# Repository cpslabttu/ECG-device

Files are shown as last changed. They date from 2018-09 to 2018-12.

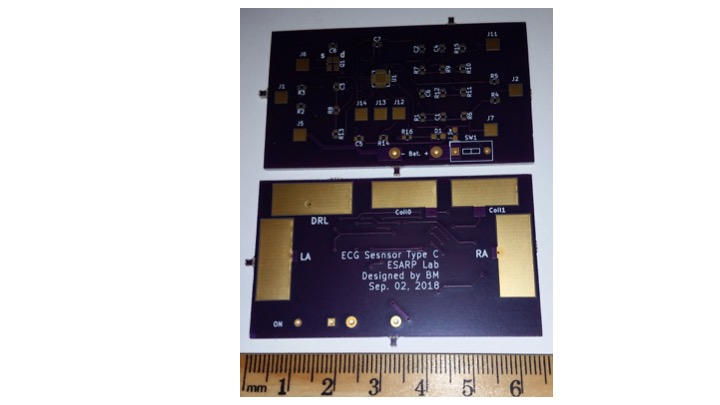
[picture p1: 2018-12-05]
Fig pcb.jpg

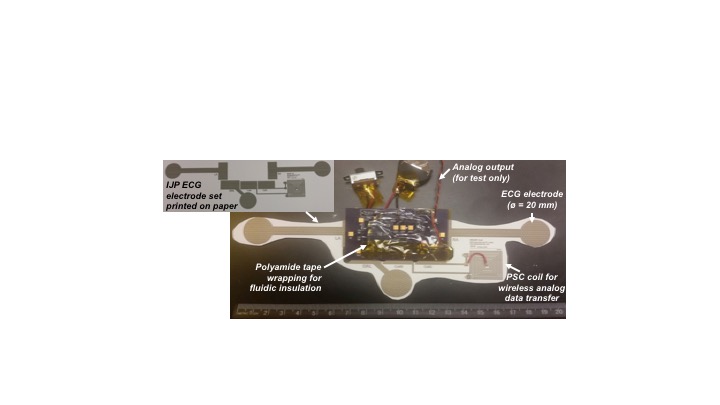
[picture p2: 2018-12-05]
Final ECG device TypeC ver1.jpeg

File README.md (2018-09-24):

# ECG-device-TypeC
Created by: Dr. B. I. Morshed, Assoc. Prof., EECE, University of Memphis, Memphis TN USA.

If using this project files, please cite:

B. I. Morshed, "Ultra Low-power Inductively Coupled Wearable ECG Sensor Design with Inkjet Printed Dry Electrodes", National Radio Science Meeting, Boulder, CO, 2019.

B. I. Morshed, B. Harmon, M. S. Zaman, M. J. Rahman, S. Afroz, and M. Rahman, "Inkjet Printed Fully-passive Body-worn Wireless Sensors for Smart and Connected Community (SCC)", J. Low Power Electron. Appl., vol. 7, no. 4, article 26, pp. 1-21, Nov. 2017.

Sergi Consul-Pacareu, and Bashir I. Morshed, "Design and analysis of a novel wireless resistive analog passive sensor technique", IET Wireless Sensor Systems, vol. 8, no. 2, pp. 45-51, 2018.

B. Noroozi and B. I. Morshed, "PSC Optimization of 13.56-MHz Resistive Wireless Analog Passive Sensors", IEEE Trans. Microwave Theory and Techniques, vol. 65, no. 9, pp. 3548-3555, Sept. 2017.

For project related info, please visit: http://www.memphis.edu/esarp/nsf_scc/index.php

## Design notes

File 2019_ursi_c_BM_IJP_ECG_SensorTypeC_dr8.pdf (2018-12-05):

# Ultra Low-power Inductively Coupled Wearable ECG Sensor Design with Inkjet Printed Dry Electrodes

Bashir I. Morshed
Electrical and Computer Engineering University of Memphis
Memphis, TN 38152 USA
bmorshed@memphis.edu

Abstract—Wearable Electrocardiogram (ECG) devices cannot be used for long duration due to power requirement (on a single charge) and electrode degradation. A new extremely low power wearable ECG sensor device is proposed in this work that minimizes power consumption by eliminating digitization and wireless data transfer with a zero power analog inductive coupling and long duration inkjet printed (IJP) dry electrodes. The prototyped device can operate on a coin cell for 140 hours consuming only 1.6 mA. Ability to collect ECG data at home for long duration can largely improve capabilities of mobile health (mHealth) towards Smart and Connected Communities (SCC).

I. INTRODUCTION
Electrocardiography (ECG/EKG) systems have progressed from large stationary bench setup to miniature wearable or body-worn systems [1]. Related challenges that are preventing further miniaturization include power consumption and long-time operation of ECG electrodes. Inkjet printing (IJP) is a new additive fabrication technology that can deposit materials (in ink form) to planar substrates (such as paper) with high precision (a few micron) achieving consistent thin film profile (in the range of micron). We have previously reported an IJP electrode for ECG data capture that operates for a long duration (several days) without degradation [2]. In this paper, we report a new design scheme for an ultra low-power wearable ECG sensor system that incorporates the IJP ECG electrodes.

II. CONCEPT
Fig. 1a shows a typical ECG sensor system that includes ECG electrodes, differential amplifier followed by filter and other analog signal processing circuitry (e.g. variable gain amplifier), an analog-to-digital converter (ADC), an optional microcontroller unit (MCU) for data buffer and management of the wireless module, and a wireless module (typically Bluetooth or BLE). In addition, if the circuit is powered with rechargeable battery (e.g. LiPo), a charge management circuitry will be needed (not shown).
Fig. 1b also shows the proposed ECG sensor system that eliminates the most power hungry element: the wireless module. Typical Bluetooth module requires 50 - 70 mA current during transmission which might be an order higher compared to other modules on the wearable ECG sensor system. Instead of the typical wireless module, we have used inductive loading principle that is developed through our Wireless Resistive Analog Sensor (WRAP) sensor research work [3,4]. Inductive loading technique does not consume any power from the sensor itself, hence leads to a low-power design. Furthermore, data through inductive loading can be transferred in analog mode (e.g. amplitude modulation), which also eliminates the need for the ADC and MCU. However, a voltage-to-impedance transducer is needed to interface the analog output and the transmitter coil, when we have realized with a single transistor.

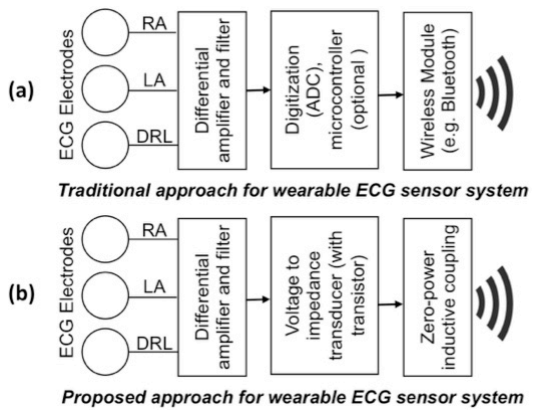
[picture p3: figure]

Fig. 1. (a) Traditional wearable ECG sensor system. (b) The proposed ECG sensor system.

III. DESIGN DESCRIPTION
Fig. 2 shows the complete KiCad schematic circuit diagram of the prototyped ECG sensor. Note that the planar spiral coil (PSC) and ECG electrodes are not part of KiCad schematic and are shown for illustration purpose only. The designed KiCad EDA files (schematic, layout, and gerber) are made open access via Github (https://github.com/esarplab/ECG-device).

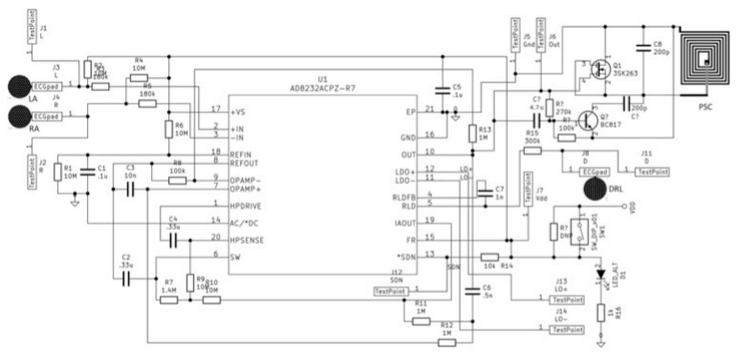
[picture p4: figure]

Fig. 2. Schematic diagram of the proposed ECG sensor. The differential amplifier, filter, and gain is performed with a commercial single-lead analog front end (AFE) integrated chip (AD8232, Analog Devices Inc.). AD8232 amplifies the ECG signals from the electrodes using the internal Instrument Amplifier (IA) and filters. The output can be applied to either a MOSFET (depletion mode) [4] or a BJT amplifier [3]. The results here are only based on the BJT amplifier. The transistor acts as a resistive load to the PSC coil for inductive coupling. The inductive coupling is probed with a scanner device (not shown here) that transmits ISM band RF signal (7 - 13.56 MHz). The modulation of envelope of the carrier signal is captured by the scanner [3].
The schematic design was used to develop a 2-layer PCB using KiCad as shown in Fig. 3. The top layer contained all the components and testpads, while the bottom layer contained 5 exposed copper plates that allow direct taping of the IJP electrodes and the PSC printed on paper. The PCB design was fabricated via Oshpark 2-layer PCB service (Oshpark LLC).

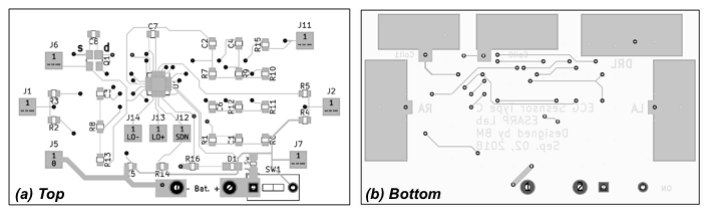
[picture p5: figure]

Fig. 3. Layout of the PCB: (a) Top layer and (b) Bottom layer. The IJP electrodes were printed with Ag nanoparticle ink (B25, Novacentrix) using an IJP printer (DMP2831, FujiFilm Dimatix Inc.) on the glossy side of a 10.4 mil photopaper (Kirkland Signature, Costco). We have previously reported details of this IJP dry electrodes [2] and PSC design [5]. The complete IJP layout contains 3 ECG electrodes (LA, RA, and DRL) and a PSC coil. We have spaced LA and RA ECG electrodes by 20 cm, but this can be easily modified and customized as per individual and ECG Lead need. This ease of personalized customization is an added advantage of the IJP process. The layout also contains the pads corresponding to the bottom layer of the PCB and attached using polyamide tape. The populated PCB with IJP electrodes and coil, along with a coin cell battery and a switch weighs only 17.9 grams (Fig. 4).

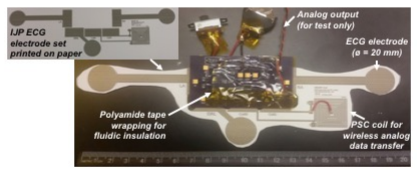
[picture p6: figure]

Fig. 4. A photograph of the fabricated and populated ECG sensor PCB attached with IJP electrodes and PSC on paper.

IV. RESULTS
The prototyped ECG device was tested and verified to collect ECG data from finger and chest configurations. Fig. 5 shows a set of data from chest configuration. The signal shows interference from utility line noise, which is removed with a 6th order Butterworth Low pass filter with fc = 40 Hz (Fig. 6). The inductively coupled signal also need and inversion operation as the envelope signal is inverted related to ECG output signal. The current consumption of the proposed ECG sensor system is only 1.6 mA, which allows a CR2032 (3V Lithium coin cell battery) to continuously operate for 140 hrs.

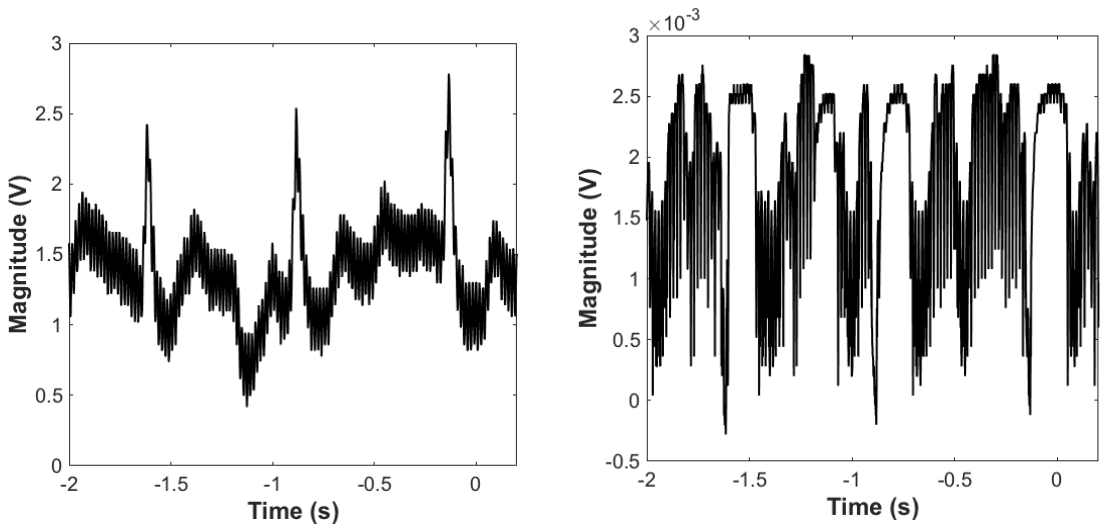
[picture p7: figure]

Fig. 5. A segment of ECG signals from the analog output (left) and from the inductively coupled envelope detector (right).

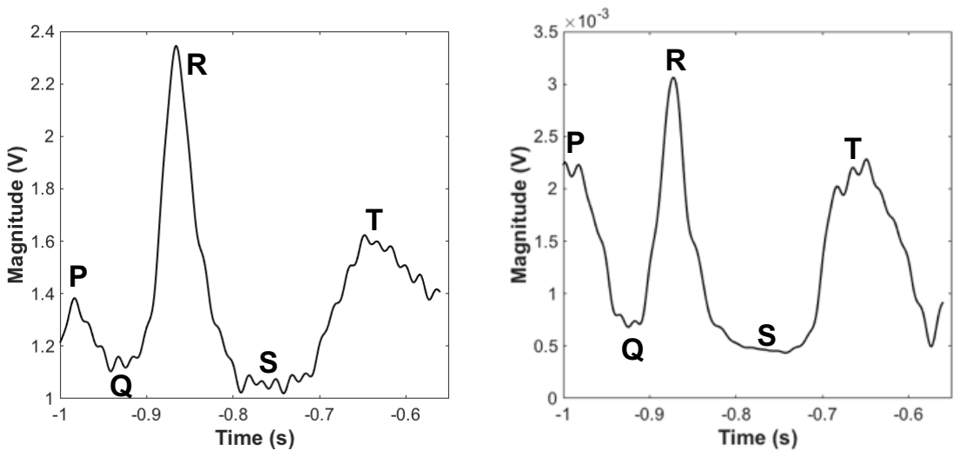
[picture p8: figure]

Fig. 6. An ECG beat from the analog output (left) and the inductively coupled signal (right) after signal processing.

V. CONCLUSIONS
We report an ultra low-power wearable ECG sensor design that uses zero-power inductive coupling and eliminates digitization and wireless transmission. We have demonstrated the prototype with IJP dry ECG electrodes to collect signals for long durations. Future work will improve the signal quality, minimize nonlinearity, optimize design, and reduce noise.

ACKNOWLEDGEMENT
This material is based upon work supported by the National Science Foundation under Grant No. 1637250 and FIT Foundation Fund Technology Development Grant 20715.

REFERENCES
[1] Y. Zheng, et al. “Unobtrusive Sensing and Wearable Devices for Health Informatics”, IEEE Trans Biomedical Engineering, vol. 61, no. 5, pp. 1538-1554, May 2014.
[2] A. Mohapatra, B. I. Morshed, S. Shamsir, and S. K. Islam, "Inkjet Printed Thin Film Electronic Traces on Paper for Low-cost Body-worn Electronic Patch Sensors", IEEE conf Body Sensor Networks (BSN), Las Vegas, NV, pp. 169-172, 2018.
[3] B. I. Morshed, B. Harmon, M. S. Zaman, M. J. Rahman, S. Afroz, and
M. Rahman, "Inkjet Printed Fully-passive Body-worn Wireless Sensors for Smart and Connected Community (SCC)", J. Low Power Electron. Appl., vol. 7, no. 4, article 26, pp. 1-21, Nov. 2017.
[4] S. Consul-Pacareu, and B. I. Morshed, "Design and analysis of a novel wireless resistive analog passive sensor technique", IET Wireless Sensor Systems, vol. 8, no. 2, pp. 45-51, 2018.
[5] B. Noroozi and B. I. Morshed, "PSC Optimization of 13.56-MHz Resistive Wireless Analog Passive Sensors", IEEE Trans. Microwave Theory and Techniques, vol. 65, no. 9, pp. 3548-3555, Sept. 2017.

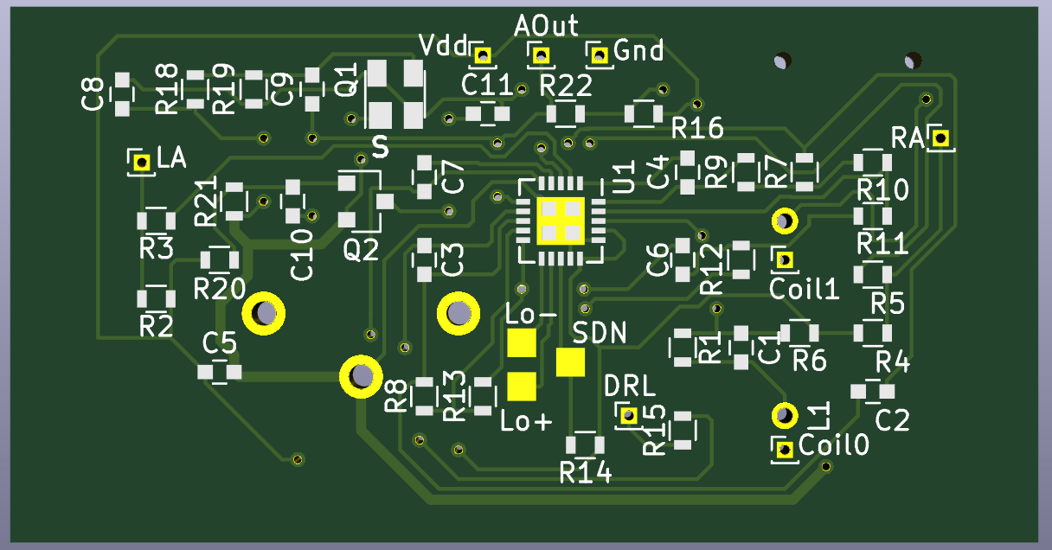
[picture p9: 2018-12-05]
ECGtypeC_V2 layout top3D.png

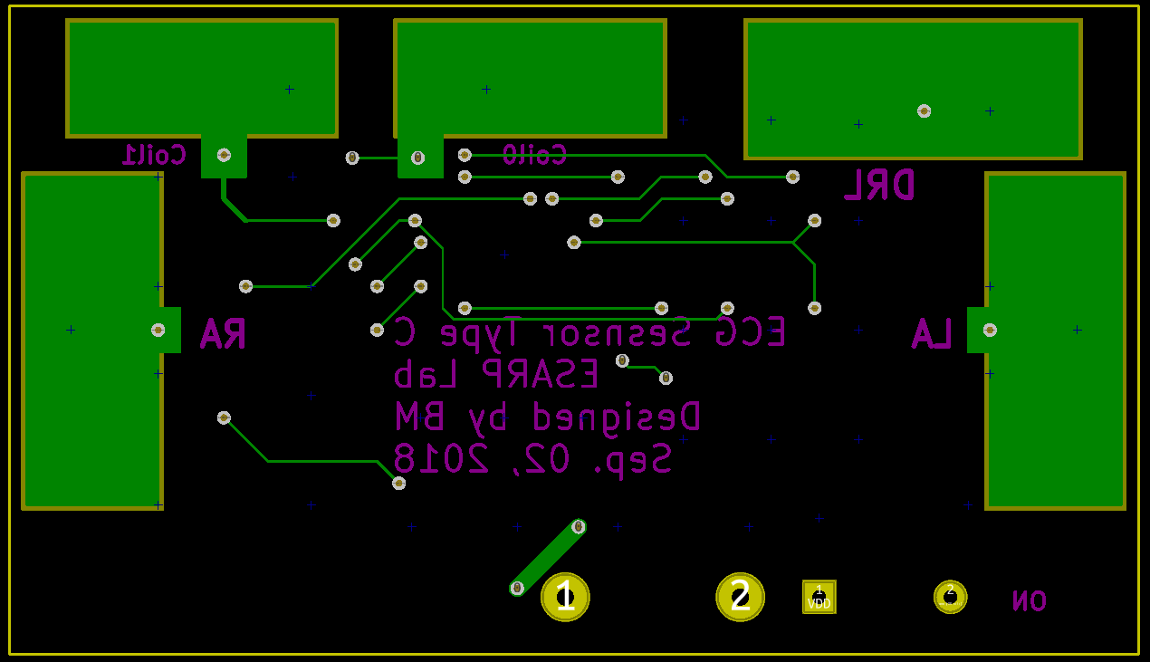
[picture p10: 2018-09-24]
ECGtypeC_layout bot.png

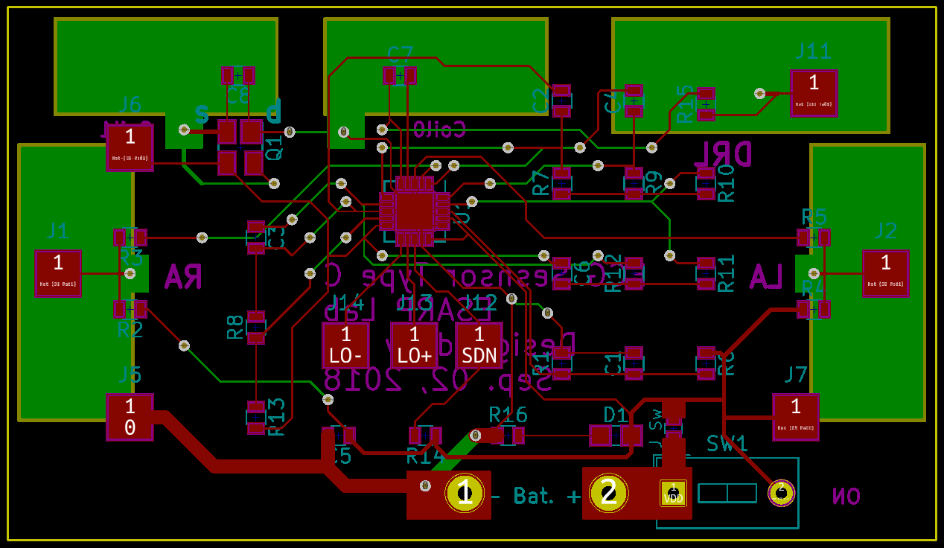
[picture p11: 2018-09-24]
ECGtypeC_layoutall.png

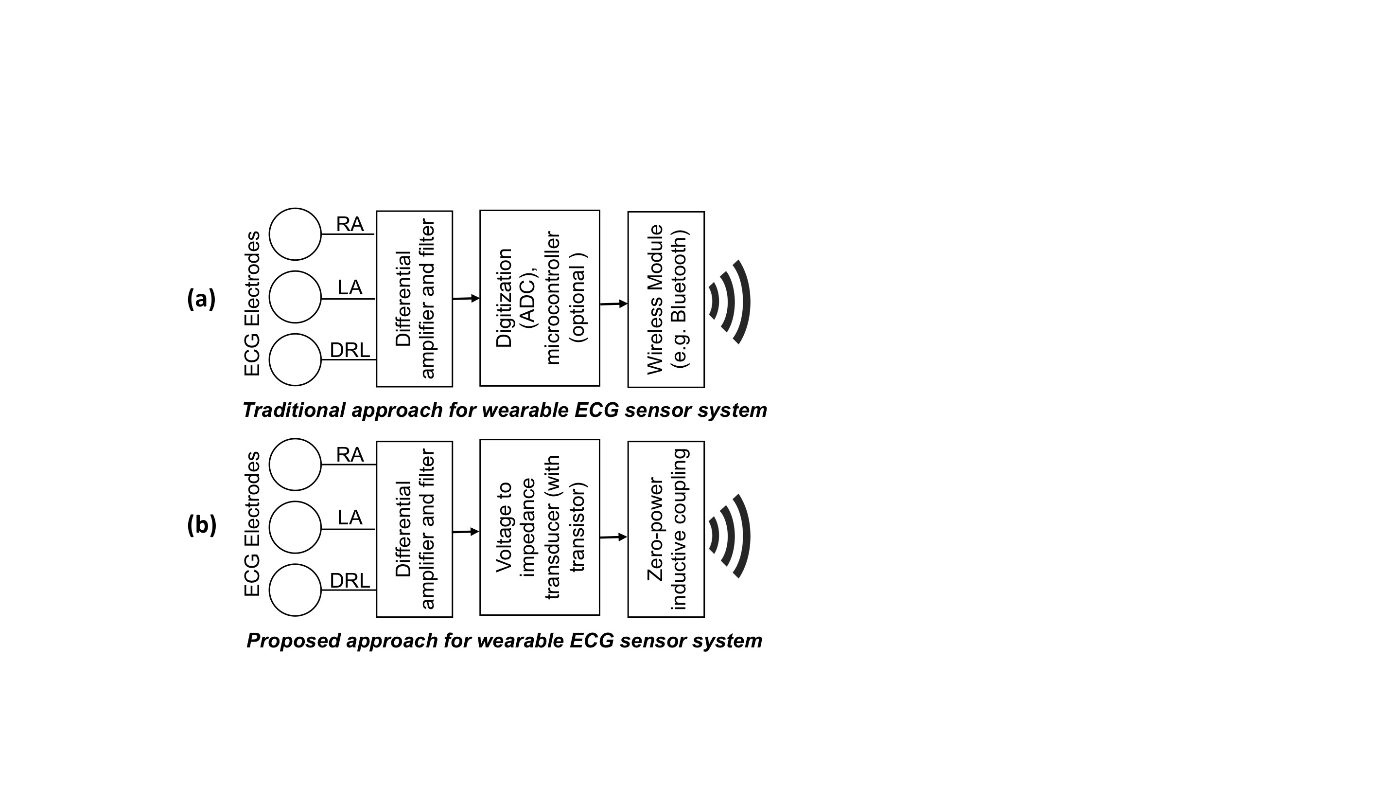
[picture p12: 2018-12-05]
Fig Block dgm ecg sensor.jpg

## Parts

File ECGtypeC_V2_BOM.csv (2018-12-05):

Id | Designator | Package | Quantity | Designation | Supplier and ref
1 | SW | SW_SPDT_CK-JS102011SAQN_BM | 1 | SW_DIP_x01
2 | Battery | CR2032V | 1 | Battery_Cell
3 | C1,C5 | C_0603 | 2 | .1u
4 | C2,C4 | C_0603 | 2 | .33u
5 | C3 | C_0603 | 1 | 10n
6 | C6 | C_0603 | 1 | .5n
7 | C7 | C_0603 | 1 | 1n
8 | C8,C11 | C_0603 | 2 | 200p
9 | C9,C10 | C_0603 | 2 | 4.7u
10 | LED | LED_0603 | 1 | LED_ALT
11 | LA | Pin_Header_Straight_1x01_Pitch1.00mm | 1 | L
12 | RA | Pin_Header_Straight_1x01_Pitch1.00mm | 1 | R
13 | LA | SolderWirePad_single_SMD_5x10mm | 1 | LA
14 | RA | SolderWirePad_single_SMD_5x10mm | 1 | RA
15 | Gnd | Pin_Header_Straight_1x01_Pitch1.00mm | 1 | Gnd
16 | AOut | Pin_Header_Straight_1x01_Pitch1.00mm | 1 | Out
17 | Vdd | Pin_Header_Straight_1x01_Pitch1.00mm | 1 | Vdd
18 | DRL | SolderWirePad_single_SMD_5x10mm | 1 | DRL
19 | Coil0 | Pin_Header_Straight_1x01_Pitch1.00mm | 1 | Coil0
20 | Coil1 | Pin_Header_Straight_1x01_Pitch1.00mm | 1 | Coil1
21 | DRL | Pin_Header_Straight_1x01_Pitch1.00mm | 1 | D
22 | SDN | Measurement_Point_Square-SMD-Pad_Small | 1 | SDN
23 | Lo+ | Measurement_Point_Square-SMD-Pad_Small | 1 | LO+
24 | Lo- | Measurement_Point_Square-SMD-Pad_Small | 1 | LO-
25 | L1 | WireConnection_0.80mmDrill_ThinPad | 1 | L
26 | Q1 | SOT-143 | 1 | 3SK263
27 | Q2 | SOT-23 | 1 | BC817
28 | R1,R2,R4,R6,R9,R10 | R_0603 | 6 | 10M
29 | R3,R5 | R_0603 | 2 | 180k
30 | R7 | R_0603 | 1 | 1.4M
31 | R8 | R_0603 | 1 | 100k
32 | R11,R12,R13 | R_0603 | 3 | 1M
33 | R14,R19,R21 | R_0603 | 3 | 10k
34 | R15 | R_0603 | 1 | 300k
35 | R16,R22 | R_0603 | 2 | 1k
36 | Itest | R_0603 | 1 | DNP
37 | R18,R20 | R_0603 | 2 | 27k
38 | U1 | QFN-20-1EP_4x4mm_Pitch0.5mm | 1 | AD8232ACPZ-R7
39 | 0 | R_0603 | 1 | R_0603

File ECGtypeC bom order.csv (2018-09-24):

Reference | Value | Footprint | Datasheet
U1 | AD8232ACPZ-R7 | Housings_DFN_QFN:QFN-20-1EP_4x4mm_Pitch0.5mm
SW1 | SW_DIP_x01 | Buttons_Switches_THT:SW_DIP_x1_W7.62mm_Slide
C4 | .33u | Resistors_SMD:R_0603
C3 | 10n | Resistors_SMD:R_0603
R9 | 10M | Resistors_SMD:R_0603
R7 | 1.4M | Resistors_SMD:R_0603
R10 | 10M | Resistors_SMD:R_0603
C2 | .33u | Resistors_SMD:R_0603
R8 | 100k | Resistors_SMD:R_0603
R13 | 1M | Resistors_SMD:R_0603
C6 | .5n | Resistors_SMD:R_0603
R12 | 1M | Resistors_SMD:R_0603
R11 | 1M | Resistors_SMD:R_0603
R6 | 10M | Resistors_SMD:R_0603
C5 | .1u | Resistors_SMD:R_0603
C1 | .1u | Resistors_SMD:R_0603
R1 | 10M | Resistors_SMD:R_0603
R14 | 10k | Resistors_SMD:R_0603
R2 | 10M | Resistors_SMD:R_0603
R4 | 10M | Resistors_SMD:R_0603
R15 | 300k | Resistors_SMD:R_0603
R3 | 180k | Resistors_SMD:R_0603
R5 | 180k | Resistors_SMD:R_0603
C7 | 1n | Resistors_SMD:R_0603
Q1 | 3SK263 | TO_SOT_Packages_SMD:SOT-143 | http://www.onsemi.com/pub_link/Collateral/EN4423-D.PDF
C8 | 200p | Resistors_SMD:R_0603
R16 | 1k | Resistors_SMD:R_0603
D1 | LED_ALT | LEDs:LED_0805
J3 | L
J4 | R
J8 | D
J9 | Coil0
J10 | Coil1
J5 | Gnd | Measurement_Points:Measurement_Point_Square-SMD-Pad_Big
J7 | Vdd | Measurement_Points:Measurement_Point_Square-SMD-Pad_Big
J6 | Out | Measurement_Points:Measurement_Point_Square-SMD-Pad_Big
J1 | L | Measurement_Points:Measurement_Point_Square-SMD-Pad_Big
J2 | R | Measurement_Points:Measurement_Point_Square-SMD-Pad_Big
J11 | D | Measurement_Points:Measurement_Point_Square-SMD-Pad_Big
BT1 | Battery_Cell | Connectors:CR2032V
J12 | SDN | Measurement_Points:Measurement_Point_Square-SMD-Pad_Big
J13 | LO+ | Measurement_Points:Measurement_Point_Square-SMD-Pad_Big
J14 | LO- | Measurement_Points:Measurement_Point_Square-SMD-Pad_Big

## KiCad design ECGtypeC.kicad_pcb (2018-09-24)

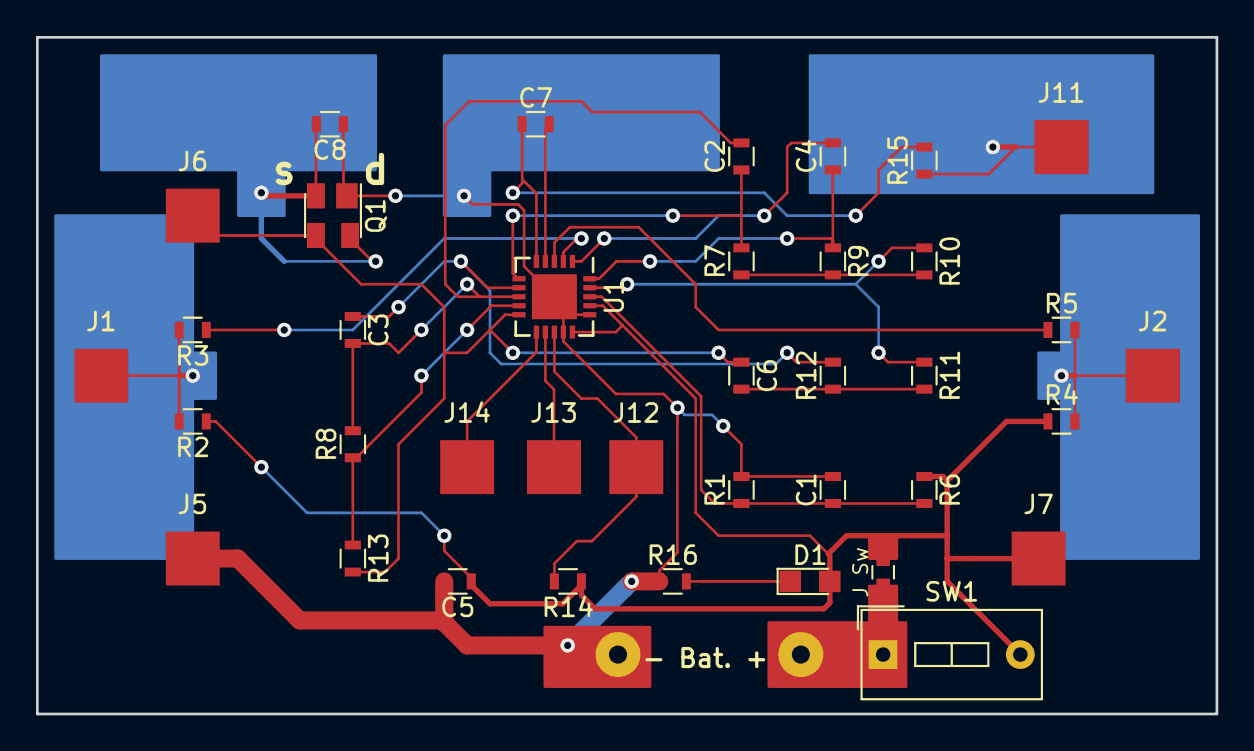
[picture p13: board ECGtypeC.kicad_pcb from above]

Board: 2 copper layers, 65.5 x 37.6 mm, 39 parts (0 on the bottom side), 25 nets.

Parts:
- Bat. +: WireConnection_1mmDrill; WireConnection_1.00mmDrill
C1, C5: .1u; R_0603
C2, C4: .33u; R_0603
C3: 10n; R_0603
C6: .5n; R_0603
C7: 1n; R_0603
C8: 200p; R_0603
D1: LED_ALT; LED_0805
J1: L; Measurement_Point_Square-SMD-Pad_Big
J2: R; Measurement_Point_Square-SMD-Pad_Big
J5: Gnd; Measurement_Point_Square-SMD-Pad_Big
J6: Out; Measurement_Point_Square-SMD-Pad_Big
J7: Vdd; Measurement_Point_Square-SMD-Pad_Big
J11: D; Measurement_Point_Square-SMD-Pad_Big
J12: SDN; Measurement_Point_Square-SMD-Pad_Big
J13: LO+; Measurement_Point_Square-SMD-Pad_Big
J14: LO-; Measurement_Point_Square-SMD-Pad_Big
J Sw: C_0603_HandSoldering
Q1: 3SK263; SOT-143
R1, R2, R4, R6, R9, R10: 10M; R_0603
R3, R5: 180k; R_0603
R7: 1.4M; R_0603
R8: 100k; R_0603
R11, R12, R13: 1M; R_0603
R14: 10k; R_0603
R15: 300k; R_0603
R16: 1k; R_0603
SW1: SW_DIP_x01; SW_DIP_x1_W7.62mm_Slide
U1: AD8232; QFN-20-1EP_4x4mm_Pitch0.5mm

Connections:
0: C1.2, C5.2, C8.1, J5.1, Q1.1, R1.2, R16.1, U1.14, U1.16, U1.21
/LO+: J13.1, U1.12
/LO-: J14.1, U1.11
/SDN: J12.1, R14.2, U1.13
unnamed: C1.1, R1.1, R6.2, U1.18
unnamed: C2.1, R7.2, U1.6
unnamed: C2.2, C3.2, R8.2, U1.8
unnamed: C3.1, R12.2, U1.7
unnamed: C4.1, R9.1, U1.20
unnamed: C4.2, U1.1
unnamed: C5.1, D1.2, J7.1, R2.1, R4.1, R6.1, R14.1, SW1.2, U1.15, U1.17
unnamed: C6.1, J6.1, Q1.3, R13.2, U1.10
unnamed: C6.2, R11.2, R12.1
unnamed: C7.1, R15.2, U1.5
unnamed: C7.2, U1.4
unnamed: C8.2, Q1.2, Q1.4
unnamed: D1.1, R16.2
unnamed: J1.1, R2.2, R3.2
unnamed: J2.1, R4.2, R5.2
unnamed: J11.1, R15.1
unnamed: R3.1, U1.2
unnamed: R5.1, U1.3
unnamed: R10.1, R11.1, U1.19
unnamed: R7.1, R9.2, R10.2
unnamed: R8.1, R13.1, U1.9
